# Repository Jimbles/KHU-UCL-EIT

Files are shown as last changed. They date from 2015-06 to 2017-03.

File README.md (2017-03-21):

# UCL KHU EIT MK2.5 MODS & MATLAB SOFTWARE

# CASE AND POWER SUPPLY

A new case and power supply had to be designed to enable the use of the 32 channel system inside a case without overheating. Included are the schematics and layout of the PCBs and the CAD drawings of the new cases

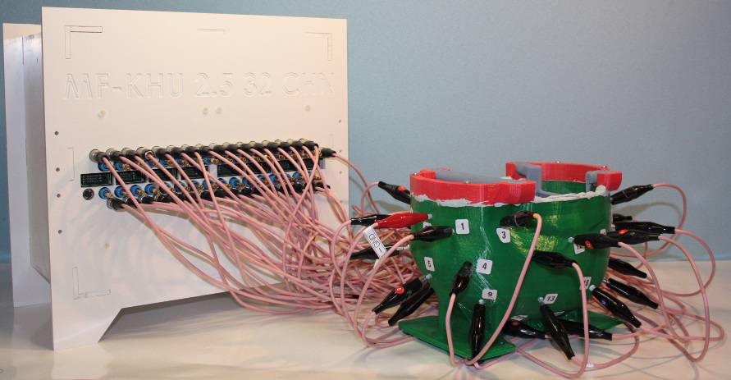
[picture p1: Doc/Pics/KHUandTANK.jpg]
khu and tank


# SOFTWARE

Software used in UCL group for making life a bit easier using the KHU Mk2.5 EIT system!

## Load_data

`khu_load.m` converts the data in a subdirectory into mV, as well as the protocol and other system settings. This is standalone, but can reference the .mat file made in `khu_makepairwise.m`

## Make_script

Most important script is `khu_makepairwise.m`, which creates the required script and proj file for the desired protocol/current/gain etc. 

## Calibration

These scripts load the calibration data located in the various .txt files generated by the KHU C++ GUI, and tries to apply some of the fuzzy logic/received wisdom from Bishal and other users

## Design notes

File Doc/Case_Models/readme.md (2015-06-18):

# 3D MODELS FOR CASE DESIGN

Included in this repo are .Step files created in Solidworks which were used to make the improved cases for the 16 chn and the 32 Chn KHU systems. All cases are made from plastic and all fixes are also insulating, so no metal parts are touchable

### 32 Chn Case

This case was cut out using a CNC machine from 4.5 mm ABS. The 4 inner pieces were glued together using acetone, with bracing pieces running along the inside edge. Drawings for CNC machine for both 32 system and power supply case found in Docs/Case_drawings ``32-CNC-Assembly.pdf``

### Power Supply Case

Constructued using similar methods to system case, with all but the lid stuck togther with bracing. To screw the lid on, corner pieces ``32PowerCaseCNR`` were 3D printed and an plastic nut added. These were then glued in all four corners with epoxy

### 16 Case
This was laser cut out of 4mm perspex - power supply could just about squeeze in the back. File used for laser cutting was ``16-Laser-assembly.pdf``

### Fans

In all cases the fans used were San Ace 120 model num ``9S1212M4001`` from farnell. These run at 12 V, so another XP Power AC/DC converter was added to the power supply case, with a separate connection to the system case

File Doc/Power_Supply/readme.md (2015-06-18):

# POWER SUPPLY

These are an adaptation of the existing power supply design, but with improved heat dissipation on the power transistors and higher current gain. A more detailed description is given in ``Power_Supply_Report.docx``

These were designed for the 32 Channel system, however they can just as well be used for the 16 Channel, and may even be beneficial

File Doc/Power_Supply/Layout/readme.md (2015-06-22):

These are the layouts of the boards designed in OrCAD. Also included are versions converted into Allegro PCB editor types, but these did not convert without problems...

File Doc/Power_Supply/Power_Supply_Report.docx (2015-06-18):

32 Channel KHU Mark 2.5 Power Supply

1. Power Supply Requirements for the 32 channel KHU Mark 2.5 system:

| Digital backplane | Analog backplane | DSP
Voltage (V) | 3.3 | +5, -5 | 5 or 7
Current (A) | 8 to 9 | 3 to 4 | 0.15 to 0.2

2. Problems with the old power supply:
- It was primarily designed for the 16 channel system hence it was unable to meet the specifications of the 32 channel system
- Since the system is power intensive, the heat dissipation is quite high. As no fans or any cooling mechanisms were included in the design, it resulted in components failure and poor performance.

Thus, the power supply had to be redesigned, building on the design of the older one.

3. Power supply design

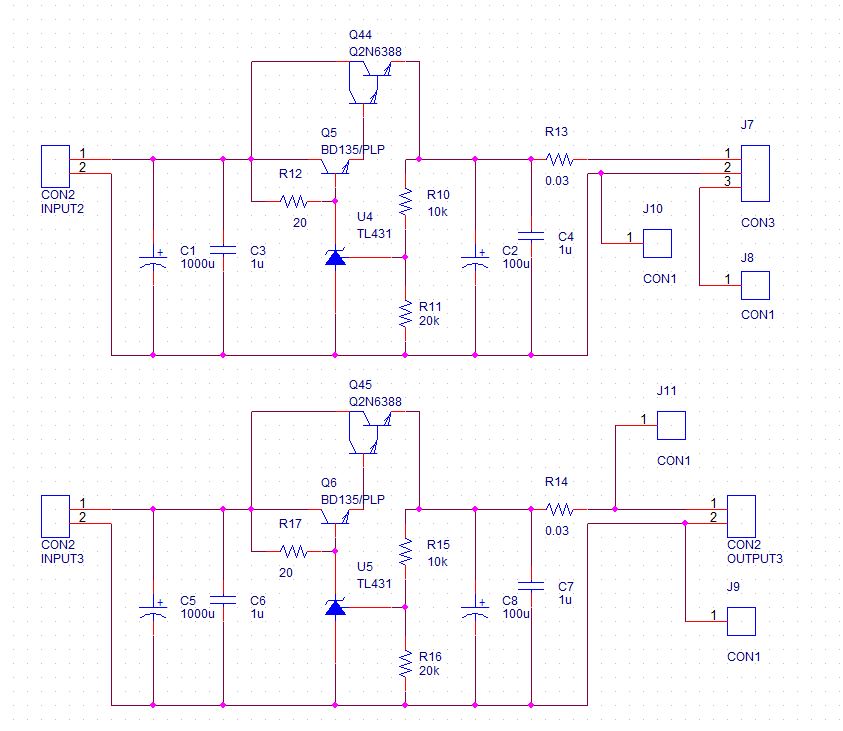
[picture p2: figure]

Figure 1: 3.3V digital power supply

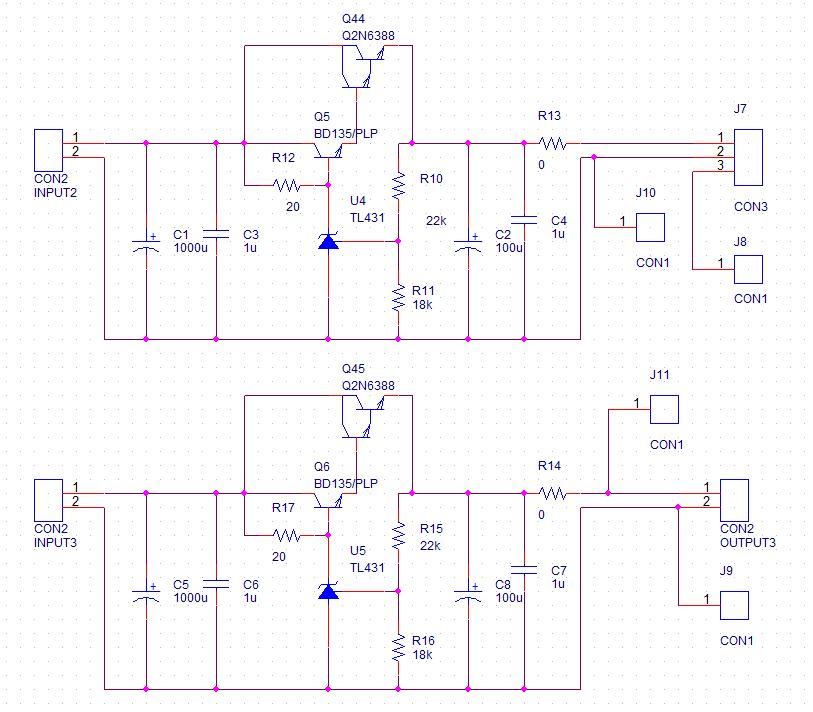
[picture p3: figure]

Figure 2: +/- 5V analog power supply

Same switching mode power supply (SMPS) modules used in the previous design were used in this new design as well. ECM100US07 (7V, 100W) is used to supply the digital backplane and the DSP, ECM100US09 (9V, 100W) is used for the analog backplane and ECM100US12 (12V, 100W) for the fans in the power supply case as well as the KHU system case.

Figure 1 and 2 show the circuits to regulate the outputs from the SMPS to meet the requirements for the system. The design is essentially similar to the older one with the exception of the capacitors and the transistors used. In order to meet the required amperage, transistors BD135 and 2N6388 were used in darlington pair configuration. 2N6388 is a single chip darlington transistor in itself.

Figure 1 and 2, which are for the digital and analog supply respectively, differ only in the value of resistors used. Two circuits in figure 1 are used in parallel to provide the higher amperage for the digital supply, hence the 0.03 ohm, 3W resistor is included at the output to balance the current. The circuits in figure 2 should be connected in series in order to obtain the +5V, GND and -5V required for the analog supply. As evident from the circuit, this is achieved by connecting J10 to J11 and J8 to J9.

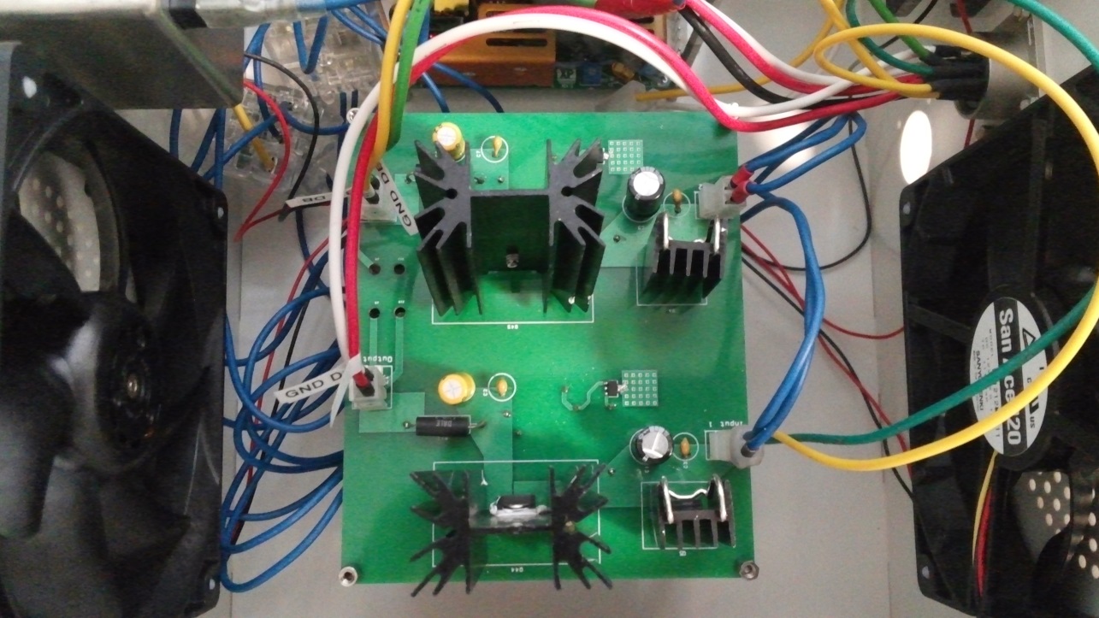
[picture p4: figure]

Figure 3: Circuit board for 3.3V supply

The layout for the circuit board has been designed to suitably accommodate the components which include large heatsinks for 2N6388, and to provide ample space for the high current path.

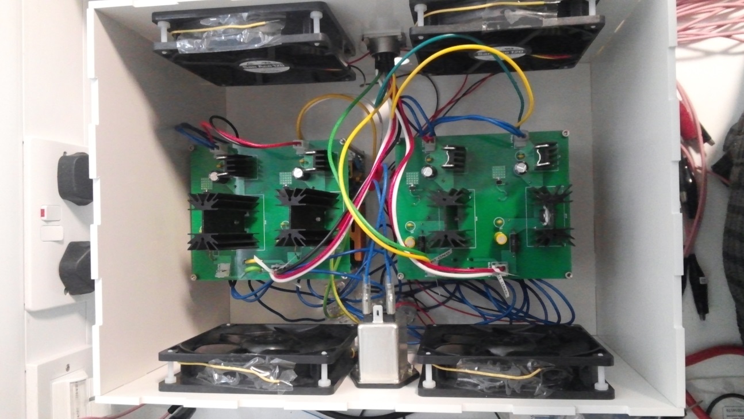
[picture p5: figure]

Figure 4: The power supply in its entirety

Two ECM100US07 modules are used to power the digital supply and two ECM100US09 modules are used to power the analog modules. One ECM100US07 is used to power the DSP. The outputs of ECM100US07 are adjusted to be 6.5 V and outputs of ECM100US09 are adjusted to be 8.5V using the potentiometer in the modules. This is done in order to reduce the power dissipation at the transistors.

Four fans are used for cooling the power supply as seen in figure 4. The fans are rated at 12 V, 0.13 A each. ECM100US12 is used to power the fans.

4. Comparisons with old power supply

Figure 5: Comparison between old and new PSU when KHU system is idle

Figure 6: Comparison between old and new PSU when KHU system is scanning

The performance of the new power supply shows significant improvement over the old one as shown by figure 5 and 6. This data was collected from the +5V and GND pin on one of the analog backplanes for the 32 channel system.

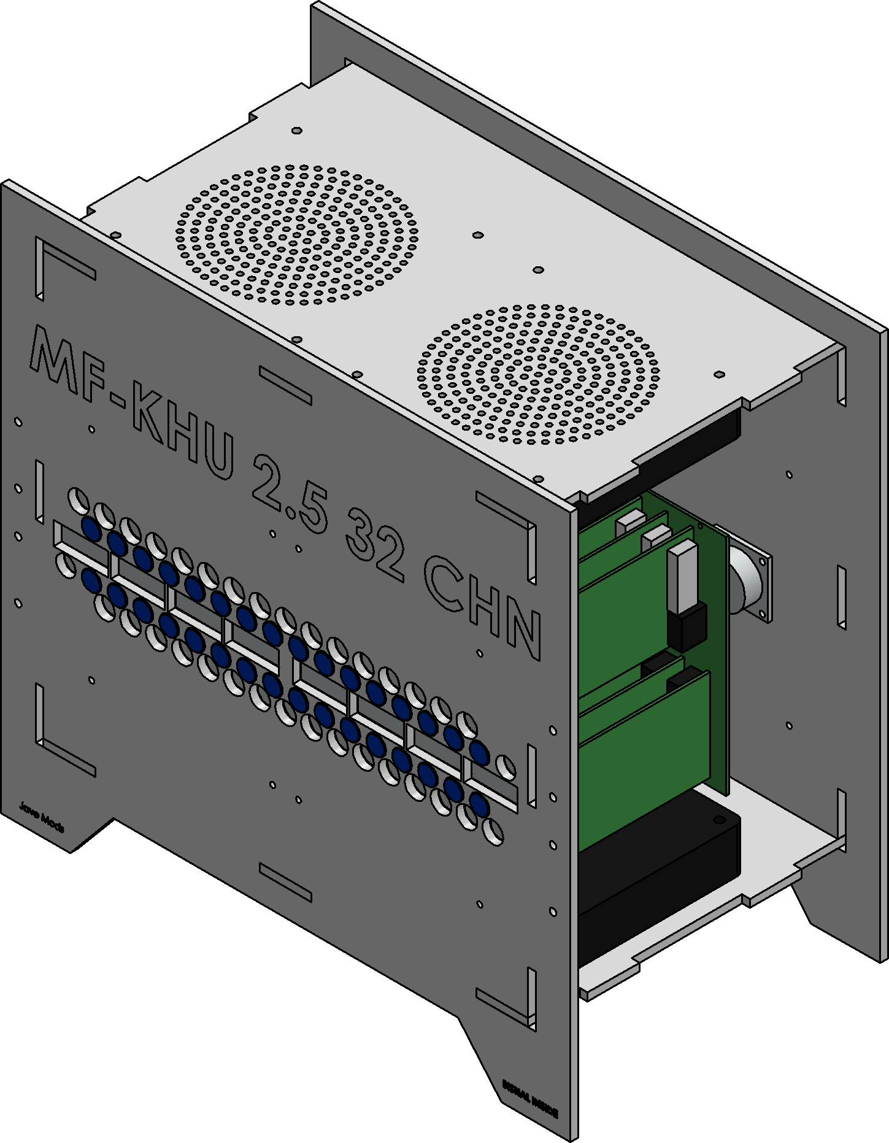
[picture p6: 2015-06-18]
Doc/Pics/32SystemCase.png

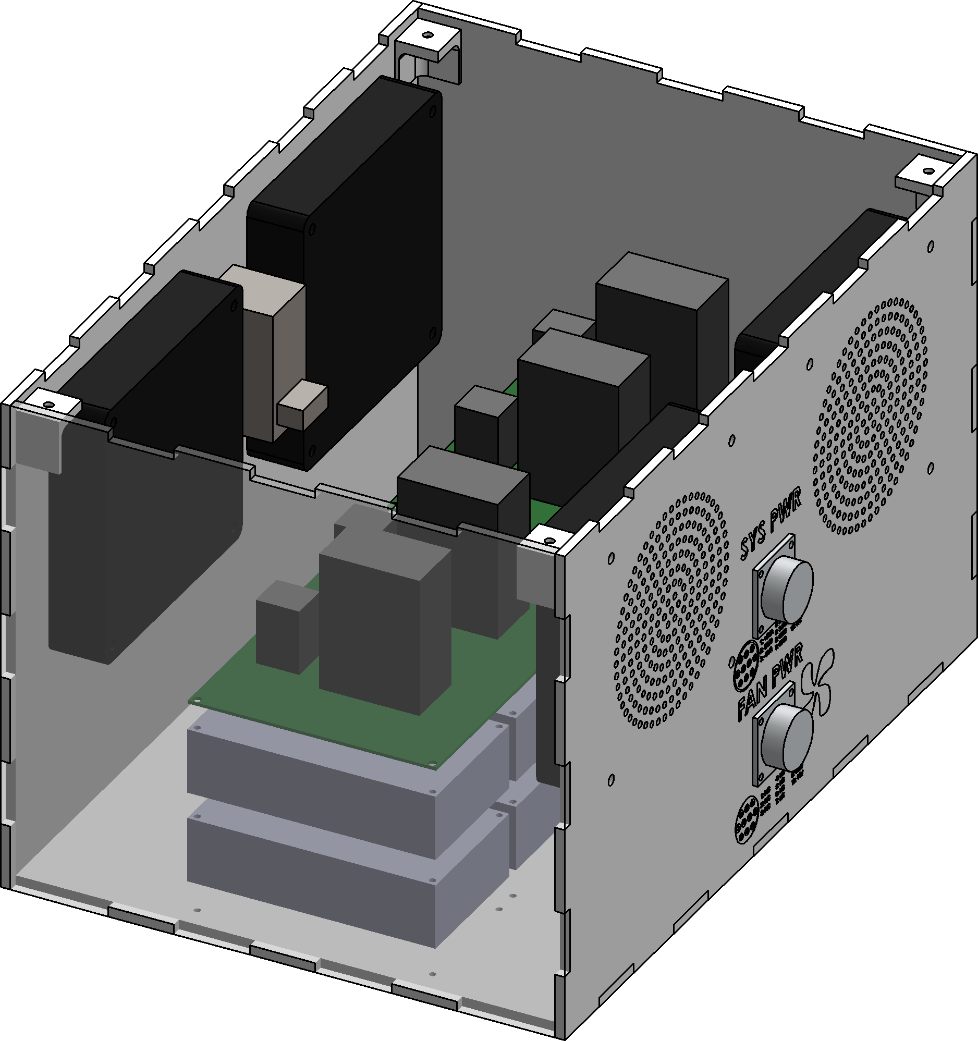
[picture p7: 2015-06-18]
Doc/Pics/32PowerCase.PNG

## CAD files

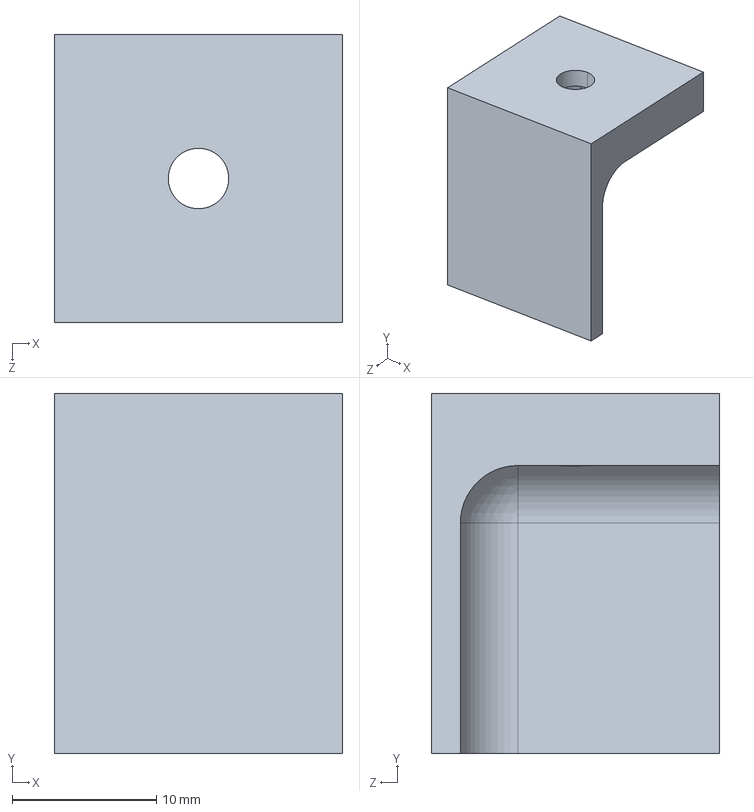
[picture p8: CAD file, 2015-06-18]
Doc/Case_Models/32PowerCaseCNR.STEP
20.0 x 25.0 x 20.0 mm

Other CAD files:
Doc/Case_Models/32PowerCaseCNR.STL

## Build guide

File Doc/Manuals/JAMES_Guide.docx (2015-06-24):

# KHU EIT MK 2.5 Calibration Procedure and System Check

This document is supposed to be used in conjunction with the manual given by Kyung Hee, which describes the cabling setup etc. This guide is more of a best practice guide, and what to look for to check that the calibration is OK and how to check the system is connected fine.

# System Check – or what to do when you get “Total Ch: 0” errors

### First Sanity Check:

Is it even connected properly? Select “Devices and printers” from the start menu and you should have USBXpress device listed under unspecified devices

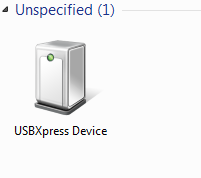
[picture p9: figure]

If that is OK then the next thing to do is check the IMM connection! If it is not, check the power to the DSP – is the light on at the back? (you will have to take the back of the case to see) Change the USB cable, check the power cable, restart the PC, try on another computer etc. etc.

## Check IMMs are recognised by the system

1. From the KHU software, select window > Engineer Control Dialog
2. On this dialogue hit USB Check, and the box to the left should change from 0 to 1.
3. Next hit Port Open, and the box should read Port Open

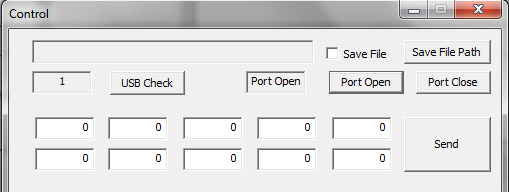
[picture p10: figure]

4. Next, with all 10 boxes with 0s in, hit send. This checks the communication is OK. The response should be: 129 and a load of zeros.

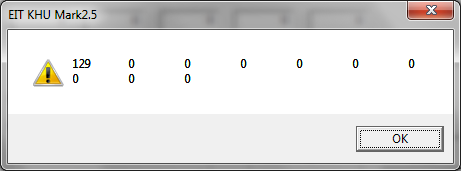
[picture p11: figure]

5. If that checks out, change the top left box to 2 and hit send like so:
6. And you should get the following response

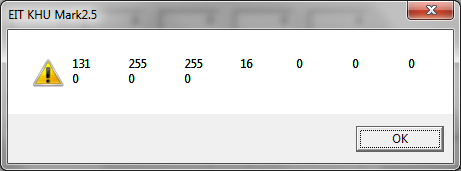
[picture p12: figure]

A little explanation:

131 is the response of the controller 129+2 (the command sent)

The next first two columns represent what channels of the digital backplane have IMMs in them as a binary number (1 for detected, 0 for undetected). The backplanes are split into 2 groups of 8, with the second column representing 1-8, and the third number representing 9-16. The response from each of the two groups is 25510 = 111111112, meaning an IMM was detected in each channel of the both groups. This is good. For example 19110 =101111112 means that an IMM was not detected in the 7th channel of that group. This is bad.

The next number are the total number of connected channels (i.e. ones with IMMs in them), which should be 16.

The final number is the total number of unconnected channels, and should be 0.

Summary:

131 | 255 | 255 | 16 | 0
System response | Group 1 connected IMMs | Group 2 connected IMMs | Total IMMs connected | Total unconnected channels

## What to do if you don’t get this!

The connections between the IMMs and the digital backplane are likely slightly loose. Take apart the system and rebuild it.

# Calibration

You have to do each of these steps for each frequency. The steps for this are pretty well documented in the proper manual.

## Order

The order in which you should perform the calibration is:

1. Output Impedance
2. DC Offset
3. Output Impedance
4. Amplitude
5. Voltmeters – Close the software afterwards. Known bug!

## Notes on cables

- Use the cables you are going to record with, i.e. the ones that will eventually be connected to the electrodes.
- Use the gold adaptors in the holes for the resistor phantom and the blue calibration channels to give something to crocodile clip on to.
- Use a short cable to connect the centre of the resistor phantom to the channel 1 or ground for amplitude and voltmeter calibration. Make sure this cable has good connection and low impedance
- The old KHU cables from the KHU MK1 and other systems, often had a resistor in the connector. So if you are using and old cable, unsolder this from the connector first

## What to check – did it calibrate OK?

The results of all of the calibrations are stored in the folder “1234” in the folder “Calibration” found in the same folder where the KHU software is stored. Within the Calibration folder look for separate folders for Amplitude, DCOffset, OutputImpedance and Voltmeter tests, as well as subfolders for each frequency.

### Output Impedance

Choose the folder corresponding to the frequency you are calibrating at, and look at the files in Log > Zout. You should see something like this:

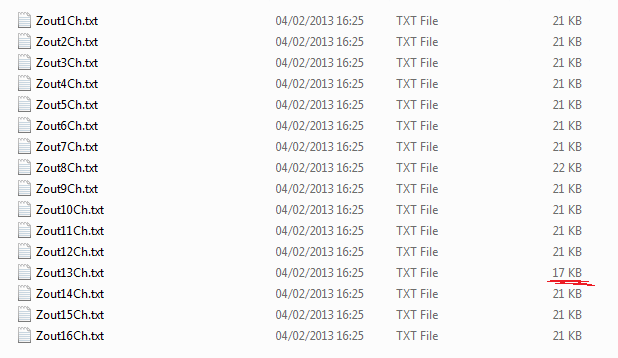
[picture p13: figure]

With a separate text file for each IMM. The first sanity check is the file size, every test is doing exactly the same thing with the same number of results, so the files should roughly be the same size. Channel 13 had a problem with the connection during this test, and this is shown by the smaller file size of 17KB as instead of 16bit numbers the results were “INF”.

Open up of these files and scroll down to the very bottom line and if all is well you should see: MaxZout: 1e+009.

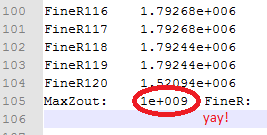
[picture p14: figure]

i.e. that the maximum output impedance was measured to be 1 MΩ. Check this for all channels before moving on.

#### If you don’t get this

Check the connections are ok, it’s usually something simple like the cables aren’t connected ok or the cable is broken. Occasionally, you might not reach an output impedance that is exactly 1MΩ but after performing the DC offset calibration and repeating this output impedance calibration can give you the correct result. If not – swap the IMMs around and see if it is consistent with the channel or the IMM.

### DC Offset

Check the DCOffset.txt in the folder corresponding to the frequencies you are interested in. What you are looking for are similar values, and only small changes – the fuzzy logic is less than 25ish with certainly no 3 digit changes.

### Amplitude

Look for the file Amplitude.txt in the folder corresponding to your frequency of interest. The first value should be 1, and the remaining values should be closed to 1, as this indicates only small adjustments to the current levels were needed. This is very sensitive to the connection to the centre of the resistor phantom, so make sure this cable is OK

### Voltmeter Calibration

The best way to check this is correct is to collect a few test frames on the resistor phantom, and compare the results with the simulation/expected results. CLOSE THE SOFTWARE AFTER VOLTMETER CALIBRATION. There is a known bug which means you can’t start scans after running that dialogue.

YOU MUST USE THE CORRECT SIMULATED VOLTAGES.

The voltmeter gives the correction factors to convert from the demodulated digital values to the simulated values (in either mV or V, or anything you choose) and to give a phase angle of 0. This includes the gain correction. Thus, if you change the gain in the protocol, you must recalibrate the voltmeters. If you change the current injection, you must first change the simulation to represent the new current level, then create a new file with the expected values, then recalibrate the voltmeters.

#### Making new simulated voltages

The model of the resistor phantom can be found in circuitlab:

https://www.circuitlab.com/circuit/m5cv9k/khu-resistor-phantom/

or as a OrCAD file in the technical folder of eit-nas.

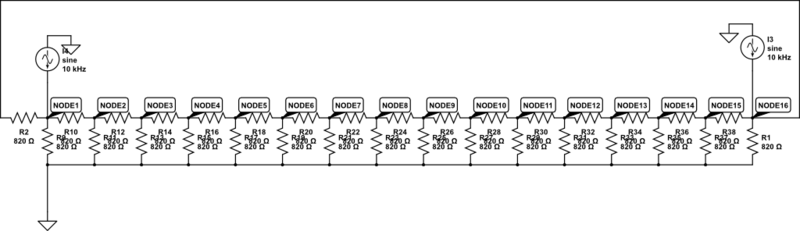
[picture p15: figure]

In this model each node represents the differential voltage between the two channels, i.e. what is measured by the system. These do not change with different protocols. So what you are interested in changing is the two current sources. These in the above picture, ch1 is the source and ch16 is the sink. The source is set to 1000uA and the sink is set to -1000uA. Change the amplitudes and the positions which match the protocol you are using, and then simulate the resulting voltages.

To get the simulated voltages into matlab to check:

1. On circuit lab, switch to the simulate panel and choose “time domain”
2. Hit “Run Time-Domain Simulation” an d you should get something pretty like this:

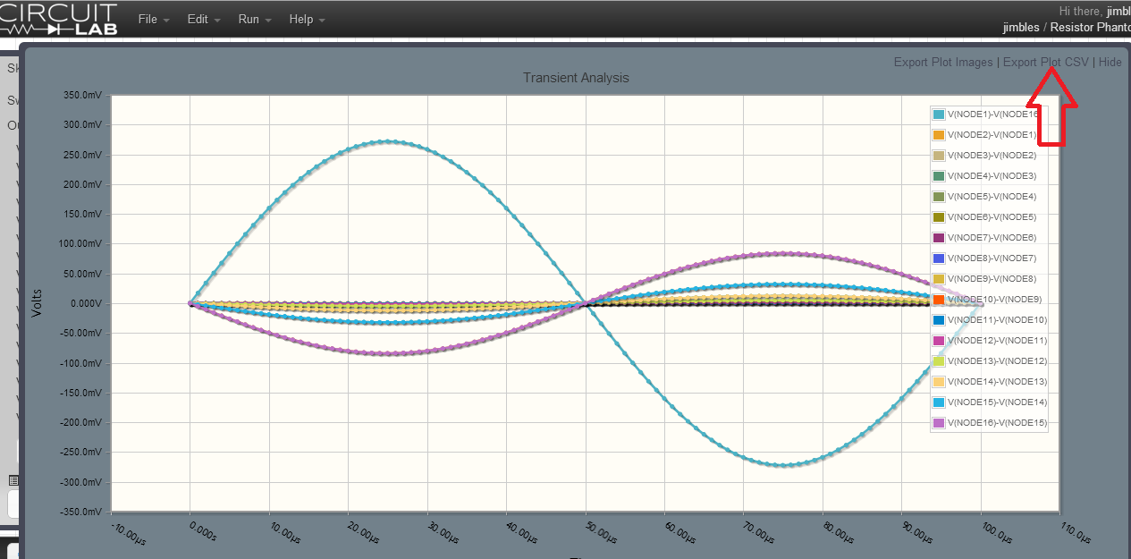
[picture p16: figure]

3. Hit Export Plot CSV and copy the text in the box that pops up to the clipboard
4. In matlab, type uiimport and then select “clipboard”, make sure comma is selected as the delimiter
5. The format of this data is then:

Time | Chn1 | Chn2 | Chn etc.

6. So to find the correct voltages for calibration find the max in each channel: max(data(:,2:end))
7. Do this for every current injection you have in your protocol
8. Make a text file in the same format as the others e.g. 2Dneighboring_mV.txt where each column is an injection pair, with a row for each channel.

# Building the system

1. Attach all the IMMs to the digital backplane
2. Holding the backplane in one hand with the IMMs vertically, align the bottom connection of analogue front plane with lowest row of 8 IMMS with the other
3. Push the IMMs together ensuring all the connectors are aligned and snapped together. This can be tricky!
4. Push the whole system together above each IMM connection with the palms of your hands
5. Attach the DSP module, check that the USB connector is parallel to the plane of the IMMs and that the pin numbers connectors on the backplane and the DSP board are matching.
6. Test the power levels are correct before connecting the system
7. Connect the power cable and test that all IMMs are recognised.
8. Unplug the power and put system in case
9. The PCB standoffs required are as followed
10. Correct PCB standoff sizes:

Front of case

10mm

Analogue backplane – 2mm

45mm

30mm

30mm

7mm

Digital backplane – 2mm

25mm (this one is optional)

7mm

Back of case

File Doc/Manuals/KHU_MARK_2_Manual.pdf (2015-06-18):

# KHU MARK 2.5 - USER MANUAL

## Contents

## I. System Description | 2

## II. Electrical Characteristics | 4

## III. Installation | 5

## IV. Operation Manual | 6

## 1. Normal mode – Single Frequency | 6

## 2. Normal mode – Multi Frequency | 8

## 3. Normal mode – Single Frequency | 6

## 4. Users configurable parameters | 10

## V. Data format | 13

## VI. Calibration | 14

## 1. DC offset calibration | 16

## 2. Output Impedance calibration | 17

## 3. Amplitude calibration | 18

## 4. Voltmeter calibration | 19

I. System descriptions

Similar to KHU Mark2 system for Electrical Impedance Tomography measurement, the KHU Mark 2.5 has two separate units, one for power supply and one for EIT data acquisition.
Current KHU Mark 2.5 is a 16- channels system with integrated calibration. Impedance measurements controller and calibration are PC-controlled through a software called EIT_Mark2.exe. It is currently only available for Windows (64 and 32 bits).

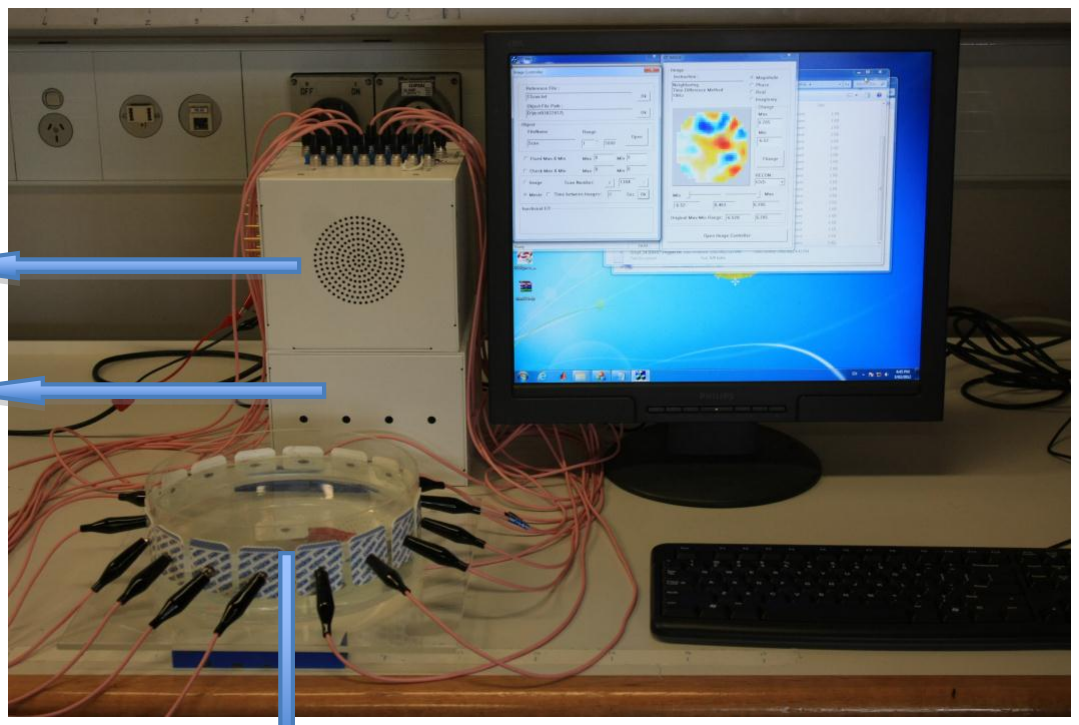
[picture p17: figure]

Figure 1 KHU MARK 2.5 system

Main KHU Mark2.5 unit consists of 16 parallel IMMs (Impedance Measurement Modules), an analogue backplane, a digital backplane and a DSP mainboard. Analogue backplane is used to switch the IMMs between current injection and voltage measurement. Digital backplane communicates between the IMMs and DSP. Each IMM consists of a CCS( constant current source) , CCS Calibration circuits, ADC (12 bits resolution), Voltage amplifier circuits and an FPGA as the central control unit for each IMM.

Main part

Power Module

Saline tank

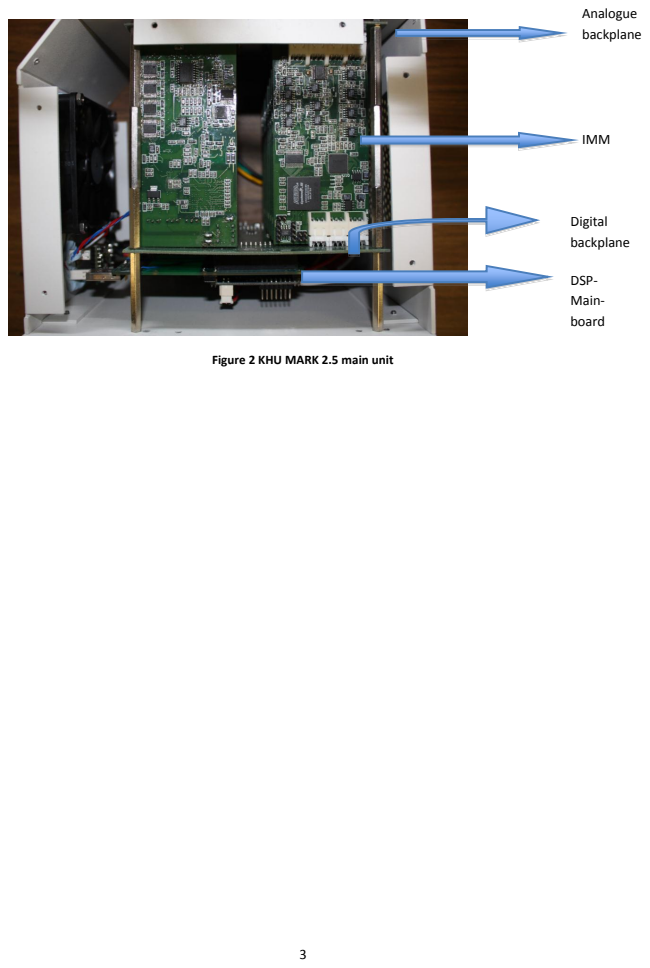
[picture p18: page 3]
IMM; Digital backplane; DSP- Main- board; Analogue backplane

Figure 2 KHU MARK 2.5 main unit

II. Electrical characteristics

### 1. Power

| The KHU Mark 2.5 is medically (?) electrically isolated to avoid electrical shock in clinical settings. The power unit provides three different types of powers to the main unit:
- ±5 VDC at 2A (max) for the analogue backplane
- + 3.3VDC at 6A (max) for the digital backplane
- +5 VDC at 1A (max) for the DSP main-board
| If the power is not functional, the following sequence should be used to provide power for the main unit of the KHU Mark 2.5 system:
- Step 0, connect main unit to PC through USB port
- Step 1, turn the ±5 VDC (2A max) on for the analogue backplane
- Step 2, turn the +3.3 VDC (6A max) on for the digital backplane
- Step 3, turn the +5 VDC (1A) max on for the DSP main-board
| When turning off the system while on lab power supply, turn off each unit in the reverse order of turning on.

### 2. Signals

- 16 parallel channels.
- 1 GND electrode
- Max current injection from each channel is 1mA
- Contact impedance (to be completed)
- Trigger signal: TTL at +3.3 V, high impedance matching (~100 kΩ)
- Operating frequencies: 10 Hz, 50 Hz, 100 Hz, 1kHz, 5kHz, 10Khz, 50KHz, 100KHz,
| 250 kHz and 500 kHz.
- The actual digital output frequencies are 11.25 Hz, 56.25 Hz, 112.5 Hz, 1.125 kHz,
| 5.625 kHz, 11.25 kHz, 56.25 kHz, 112.5 kHz, 247.5 kHz and 450 kHz.

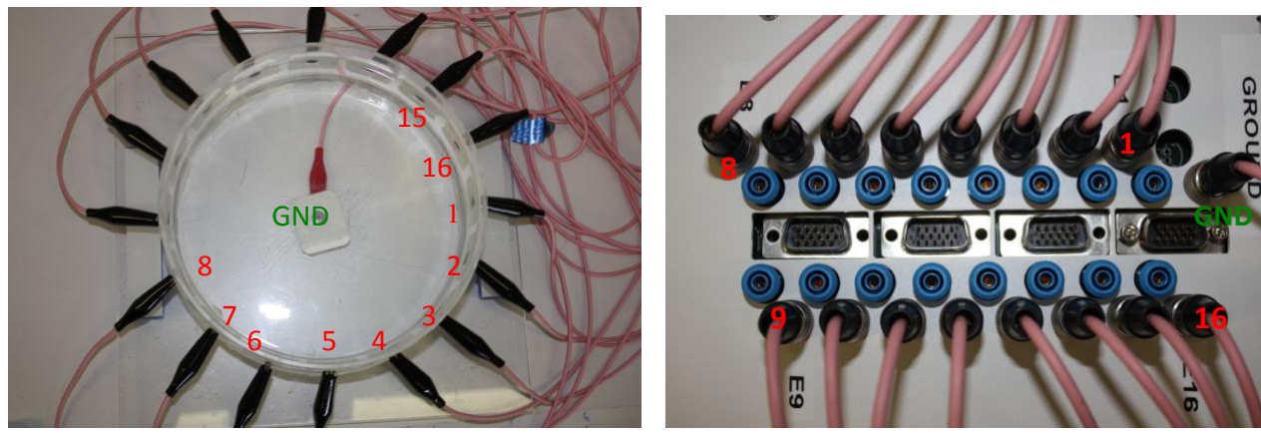
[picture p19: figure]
GND
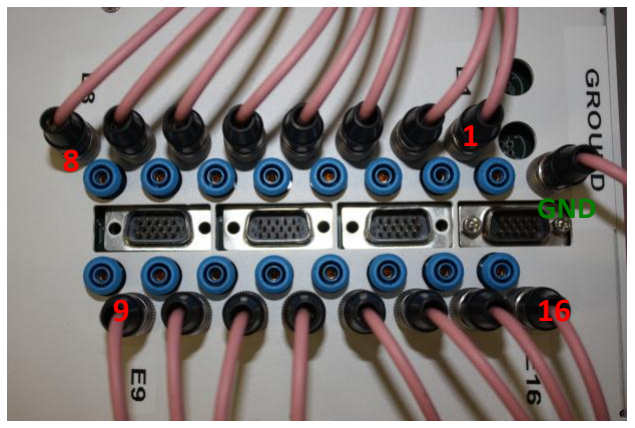
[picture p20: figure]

Figure 3 Electrodes placements on simulation tank and KHU Mark 2.5

III. Installation

### 1. USB Driver installation

USB driver of the KHU Mark 2.5 should be installed through the following steps:

1. Uninstall any preinstalled USBXPress driver
2. Run the executable USBXPress.exe. This should create and copy files to a folder at C:\SiLabs\MCU\USBXPress

In case there is no "SIUSBXp.dll" in C:\WINDOWS\system, copy SIUSBXp.dll from C:\SiLabs\MCU\USBXpress\USBXpress_API\Host to C:\WINDOWS\system

3. Run C:/SiLabs/MCU/USBXpress/Driver/Preinstaller.exe
4. Connect the system (MARK 2.5) to USB port
5. | When | the | windows | popup | asking | for | new | driver, | add | the | path
C:/SiLabs/MCU/USBXpress/Driver to find driver
6. Done. Windows should report driver for device installed properly.

Note that only the most current USBXPress driver (version < 3.5) would work in a Windows 7, 64 bits.

### 2. Setup KHU Mark2.5

i. Connect the power unit to the main unit (power should be off)

ii. Connect the main unit to PC via USB port

iii. Connect power unit to power plug (make sure power button is still off)

iv. Turn power on

v. Open the controlling software EIT_Mark2.exe

IV. Operation manual

### 3. Normal mode – Single frequency

i. EIT_Mark2 main window should look like this.

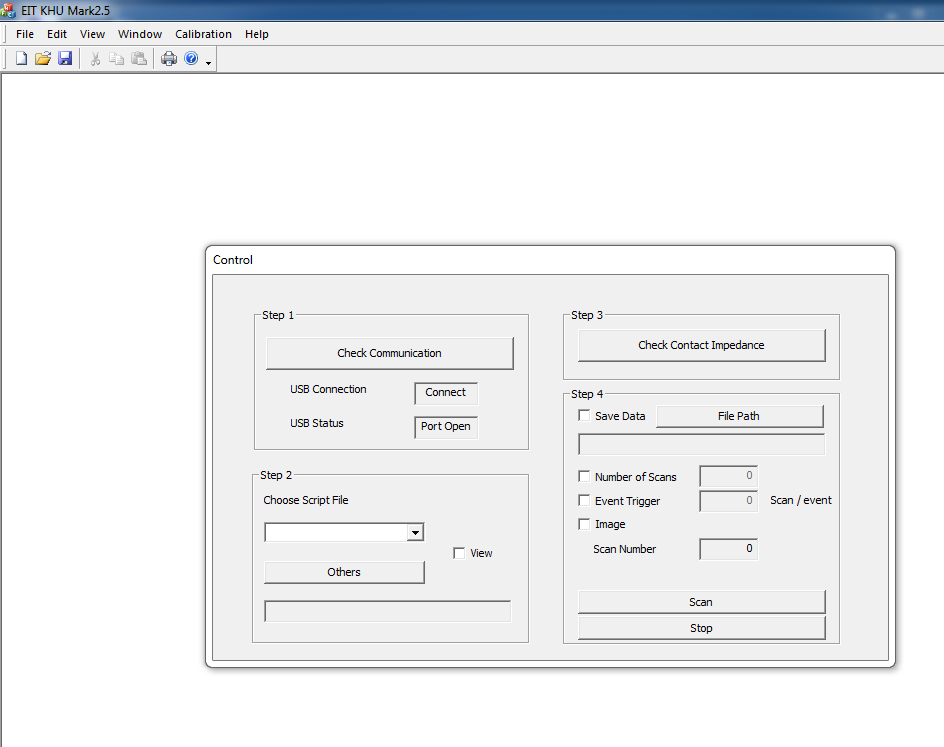
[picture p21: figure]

ii. Follow the steps on the main control dialog to setup the projections prior to scanning:
a. Step 1. Check communication, make sure the USB connection is Connected and USB port status is Open
b. Step 2. Load the correct script file with desired frequency, projection protocol, amplitude and all the calibrations are ON. An example script file is included below.

%Date 10/22/2010

%Comment :

#include "projection\projection_7.50kHz.txt"

start

setting

Channel | 16 // Number of channel
Average | 64 // Number of average
Freq | 1 | // Number of frequency
TimeInfoHigh | 0 | // Delay between projections (High byte)
TimeInfoMid | 7 | // Delay between projections (Mid byte)
TimeInfoLow | 0 | // Delay between projections (Low byte)
InjDelayHigh | 0 | // Delay from the press of Start button to
| | the start first scan (High byte)
InjDelayLow | 60 // Low byte of the above quantity

stop

calibration

DCOffset | ON
OutputImpedance | ON

Amplitude | ON
Voltmeter | ON
Protocol | 2DNeighboring_mV

stop

scan

projection1

projection2

projection3

projection4

projection5

projection6

projection7

projection8

projection9

projection10

projection11

projection12

projection13

projection14

projection15

projection16

stop

end
c. Step 3 Check contact impedance – Make sure that the voltage is not overflowed.
d. Step 4
- Check the appropriate boxes to Save data (in appropriate File Path)
- Check the box for Number of Scan and specified and the desired number of scans
- In normal mode, the Event Trigger box should be left unchecked.
- Check the Image box to view real time images. If this option is checked, during data acquisition, images are concurrently reconstructed. Typically, the first 5 scans contains transient noise and therefore are discarded (not saved). The reconstruction algorithm uses the first saved frame of data as its homogeneous or baseline data. Subsequent scans are reconstructed against the homogeneous data. Notably, the reconstruction software assumes that the object is circular, with the first electrode at 3 o’clock and electrodes are arranged clockwise.
e. Step 5 - Click Scan to start scanning, if the Image box is checked, it should look like this

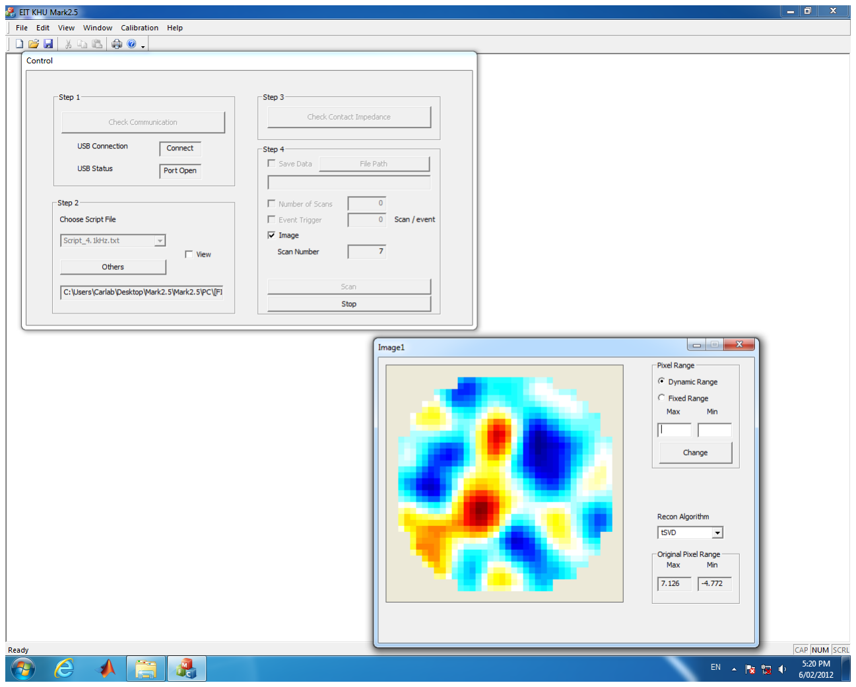
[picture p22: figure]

### 4. Normal Mode – Multi-frequency

a. Multi-Frequency mode

One main difference of KHU MARK 2.5 from KHU Mark1 is that each IMM has independent current source so that each channel can independently generate current waveform. One option is the Multi-frequency mode. As you are able to check in a projection file, injecting one frequency at one pair of channels and another frequency at the other pair of channels at the same time. Due to the fundamental method of wave generation, we have harmonic problem at Multi- frequency mode. In order to minimize this effect, it is recommended to use one pair and the other pair at the opposite end such as 1 and 16 for one frequency, 8 and 9 for the other.

Due to the limitation of bits of demodulation frequency (6-bit), it is not possible to produce concurrently produce two frequencies that have a ratio (f1/f2) of more than 50.

Multi-frequency mode can be selected in the projection.txt file. An example is shown in the following figure.

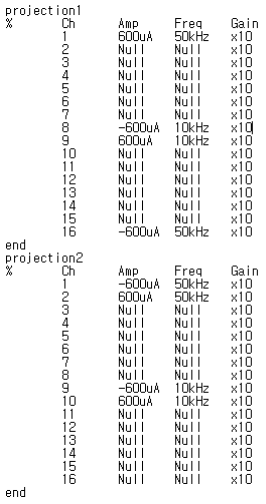
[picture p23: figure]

b. Mixed-Frequency mode

The other option of independent current source is Mixed Frequency mode. It is possible to generate the waveform by mixing three frequencies together in one channel. The ratio of frequencies in each mix is fixed at 1:5:10. Accordingly, there are four combinations from the range of operating frequency such as 10Hz, 50Hz, 100Hz (called as MIXED1), 1kHz, 5kHz, 10kHz (called as MIXED2), 10kHz, 50kHz, 100kHz (called as MIXED3), 50kHz, 250kHz, 500kHz(called as MIXED4).

In terms of GIC, the current output is connected to the GIC for smallest frequency, for example GIC3 for MIXED4.

To select mixed-frequency mode, a mixed combination (e.g MIXED1) should be entered in place of frequency in a projection.txt file, as shown in the following figure.

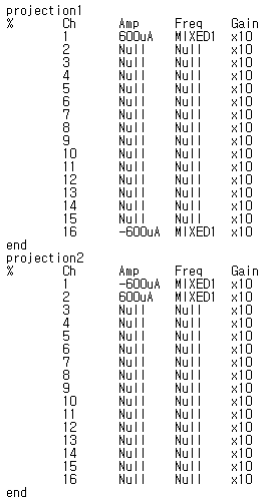
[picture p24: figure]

### 5. Biopotential triggering mode

a. Triggering signal requirements
- TTL interface (3.3 VDC)
- 5ms pulse width
- 1 Hz
b. Parameters
Inj Frequency | No Average | TimeInfo | TimeSlot | Max Frame/s
10 kHz | 1 | 0-0-127 | 1 (corr. 20 ms) | 50
50 kHz | 1 | 0-0-127 | 1 (corr. 20 ms) | 50
c. Procedures
i. Follow all the steps for normal operation mode
ii. Check the Event Trigger box
iii. Specify the number of Scans/trigger. If number of Scans/trigger is not specified, the default value is 1.
iv. Press Start to start scanning.

### 6. Users configurable parameters (in script.txt and projection.txt)

a. Script file

Users can change following quantities in the script.txt file:
-Average: Number of averages taken per voltage measurement. Minimum average is 1 and maximum is 64 and averages must be power of 2.

-Frequency: Number of frequencies to be used in each projection. This quantity should be 1 for single frequency measurement, 2 for multi-frequency mode and 3 for mixed-frequency mode.

-TimeInfoHigh and TimeInfoLow: Delay between projections. This is a 16 bits value. The first (HIGH) byte is specified in TimeInfoHigh while the second (LOW) byte is specified in TimeInfoLow.

-InjDelayHigh and InjDelayLow: Delay from the press of Start button (in the control dialog) to the start of the first scan. Similar to TimeInfo, it is a 16-bit value, specified by InjDelayHigh for the HIGH byte and InjDelayLow for the LOW byte.

The following diagram shows the timing of the system:

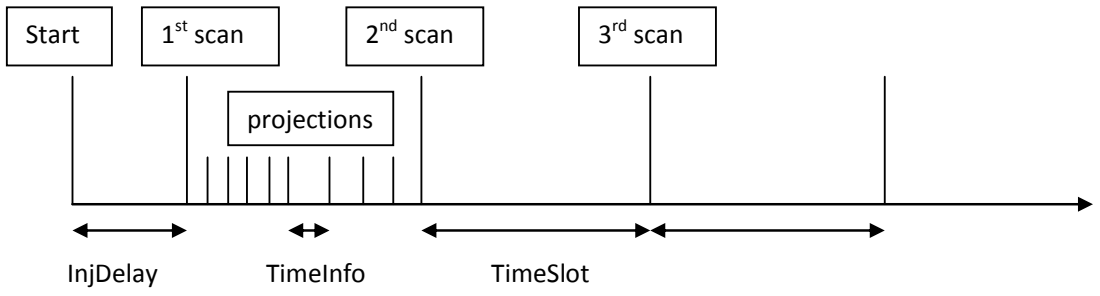
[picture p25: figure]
Start; st scan; nd scan; projections; InjDelay; rd scan; TimeInfo; TimeSlot

The InjDelay in real time min value is 80us and maximum is 360 us. Note that the values specified in the script.txt file for InjDelay and TimeInfo are digital values, not real time values.

The order of the projections can also be changed in script file.

b. Projection file
Each projection file contains the injection and measurement information for each projection, which should like this:

projection1
% | Ch Amp | Freq | Gain
1 | 600uA 50kHz x10
2 | Null | Null | x10
3 | Null | Null | x10
4 | Null | Null | x10
5 | Null | Null | x10
6 | Null | Null | x10
7 | Null | Null | x10
8 | Null | Null | x10

9 | Null | Null | x10
10 Null | Null | x10
11 Null | Null | x10
12 Null | Null | x10
13 Null | Null | x10
14 Null | Null | x10
15 Null | Null | x10
16 -600uA 50kHz x10
end
projection2
% | Ch Amp | Freq | Gain
1 | -600uA 50kHz x10
2 | 600uA 50kHz x10
3 | Null | Null | x10
4 | Null | Null | x10
5 | Null | Null | x10
6 | Null | Null | x10
7 | Null | Null | x10
8 | Null | Null | x10
9 | Null | Null | x10
10 Null | Null | x10
11 Null | Null | x10
12 Null | Null | x10
13 Null | Null | x10
14 Null | Null | x10
15 Null | Null | x10
16 Null | Null | x10
End

Typically, there are 16 projections for each frame, which are described in the projection file.

The users can change the injection pair, current injection frequency and the gain of each projection. The sequence of injection can also be changed as consequence.

Current injection amplitude and frequency can be changed in the projection file. Injection current amplitude ranges from 0 to1023 (digital value to be input): 0 digital value corresponds to 30 uA actual current amplitude, 1023 digital value corresponds to 1000 uA.

The gain is a digital value, specified the voltage gain of each voltage measurement. Minimum gain is 0 (which doesn’t mean a gain of 0). Maximum value for gain is 255.

Gactual =

40*Gdigital
200

V. Data format
Data obtained in each scan is recorded in an XXScan.txt file, saved in the folder specified in the File Path field (see Normal Operation – Single Frequency section). A part of a typical XXScan.txt would look like this:
0 | 1 | -26937.000000 | 30554.000000
1 | 1 | 26563.000000 | -30857.000000
2 | 1 | 3798.000000 | -1742.000000
3 | 0 | -1352.000000 | 1217.000000
4 | 0 | -1540.000000 | -235.000000
5 | 1 | 1545.000000 | 1705.000000
6 | 0 | -2219.000000 | 183.000000
7 | 0 | 2701.000000 | -2473.000000
8 | 0 | -933.000000 | -218.000000
9 | 0 | 566.000000 | -595.000000
10 | 0 | 151.000000 | 983.000000
11 | 0 | 841.000000 | -1982.000000
12 | 0 | -1714.000000 | 1780.000000
13 | 0 | -298.000000 | 48.000000
14 | 1 | -0.000000 | -0.000000
15 | 1 | 27005.000000 | -30445.000000

Each text file contains the data of each full frame, typically consists of 16 projections for single frequency measurement mode. The above is data obtained from one projection.
- The first column is the number of measurement: 0 is the measurement between electrodes 16 and 1, 1 is measurement between electrodes 1 and 2 and so on.
- The second column contains binary values indicating whether the corresponding voltage measurement is saturated (1) or not (0). Voltage measurements are usually saturated at the measurements involving the current injection electrodes.
- The third column contains the real values of the corresponding measurements
- The fourth column contains the imaginary values of the corresponding measurements.
In the current version of the EIT software, if multi-frequency mode is selected (specified in projection.txt file), the data is stored for the lowest frequency first (16 measurements x 16 projections), a blank line, then the data for the second lowest frequency (16 measurements x 16 projections) and so on. In total, there are 16 measurements x 16 projections x N number of frequencies.

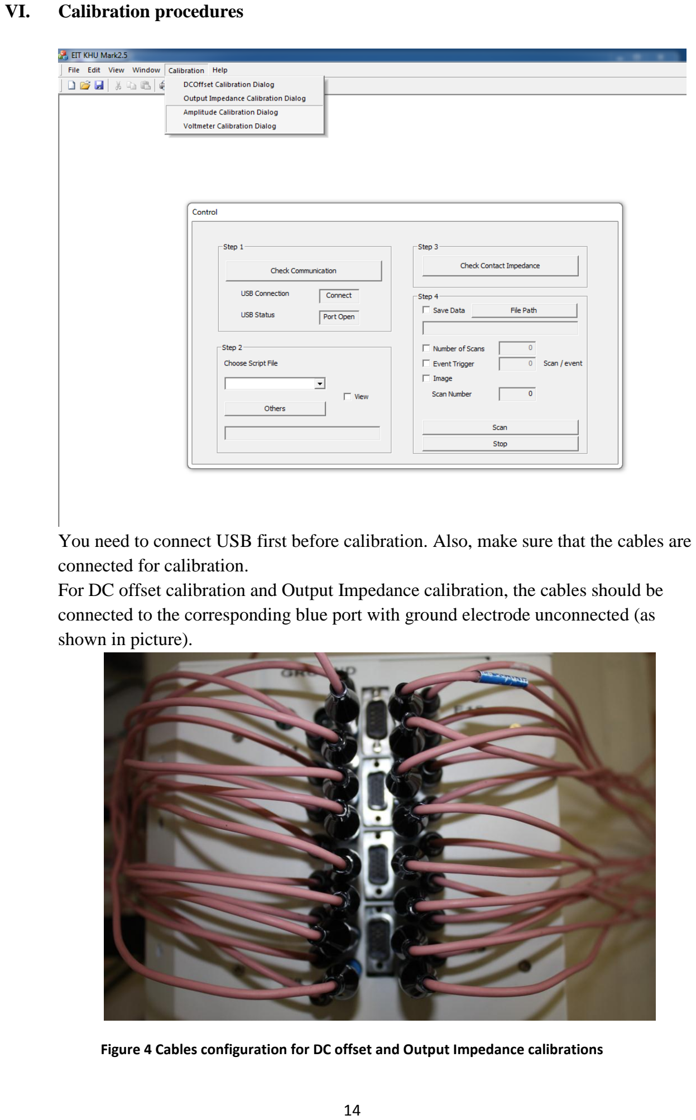
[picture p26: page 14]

VI. Calibration procedures

You need to connect USB first before calibration. Also, make sure that the cables are connected for calibration.
For DC offset calibration and Output Impedance calibration, the cables should be connected to the corresponding blue port with ground electrode unconnected (as shown in picture).

Figure 4 Cables configuration for DC offset and Output Impedance calibrations

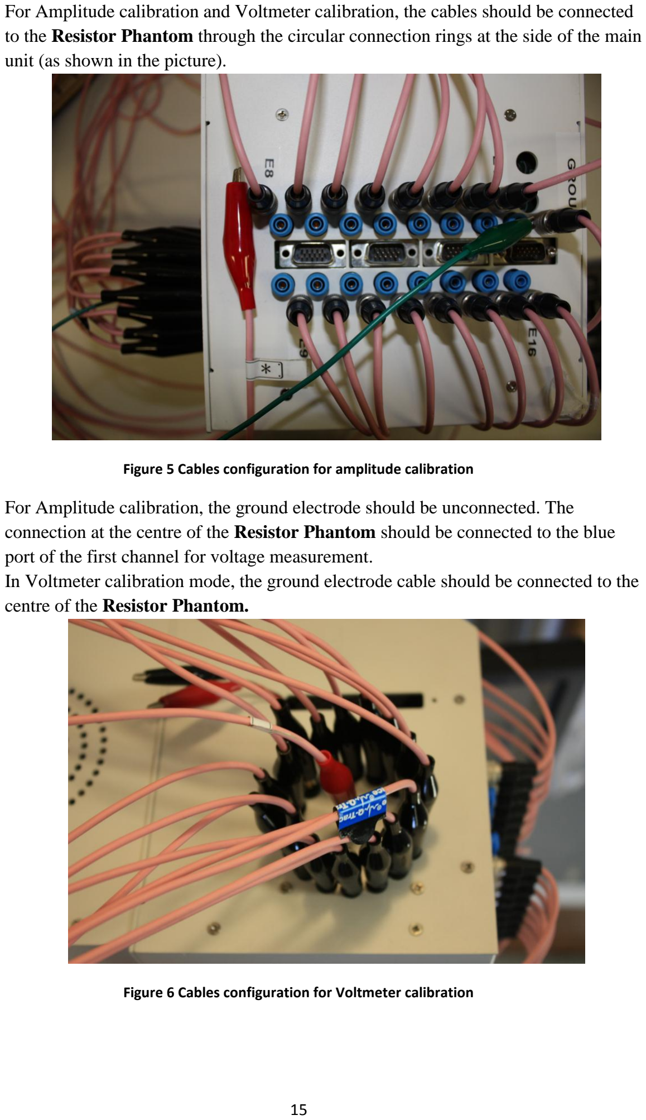
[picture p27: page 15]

For Amplitude calibration and Voltmeter calibration, the cables should be connected to the Resistor Phantom through the circular connection rings at the side of the main unit (as shown in the picture).

Figure 5 Cables configuration for amplitude calibration

For Amplitude calibration, the ground electrode should be unconnected. The connection at the centre of the Resistor Phantom should be connected to the blue port of the first channel for voltage measurement.
In Voltmeter calibration mode, the ground electrode cable should be connected to the centre of the Resistor Phantom.

Figure 6 Cables configuration for Voltmeter calibration

### 1. DC offset calibration

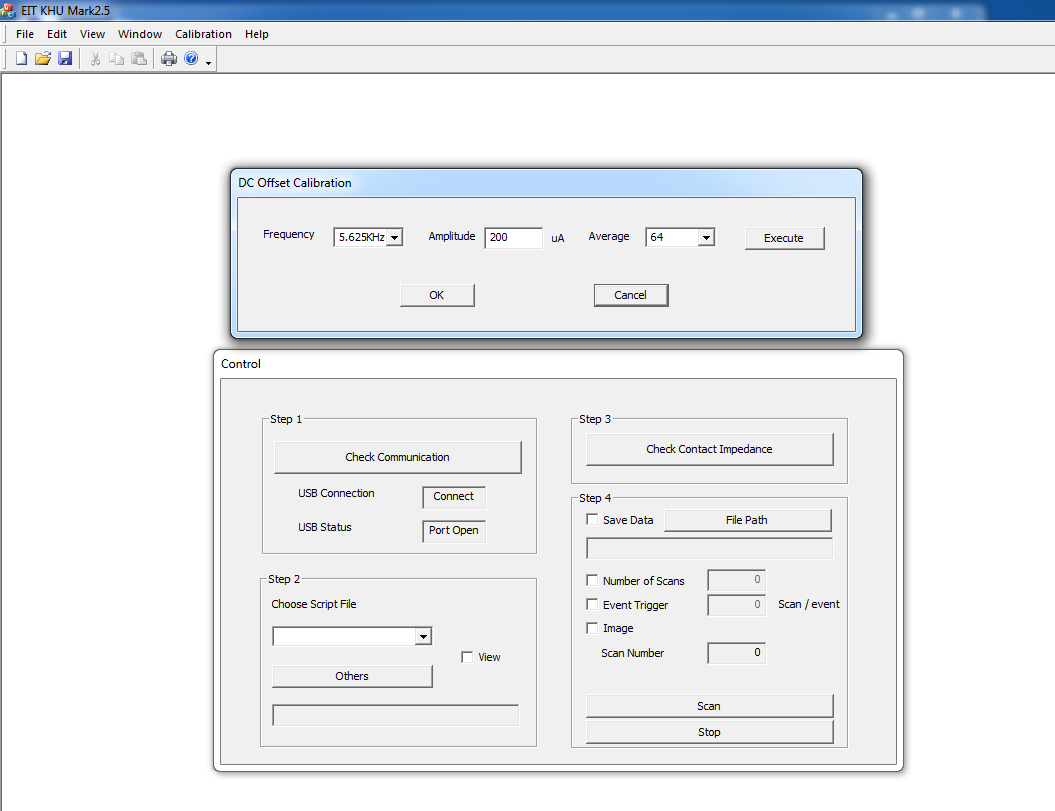
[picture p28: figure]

ii. Select frequency you want to calibrate.
iii. Set current amplitude of waveform. Default value is 200uA. It is recommended for you to set 200 as amplitude to avoid voltage saturation.
iv. Select Average number you want.
v. Make sure the cables are arranged appropriately (as shown above). vi. Press the Execute.
vii. Once the program report calibration finished. Check the saved log at RootLocation\[FINAL_SYDNEY]EIT_Mark25_20120202\Release\Cali bration\eit4\DCOffset\(CalibratedFrequency)KHz\DCOffset.txt to make sure calibration is successful.

### 2. Output Impedance calibration

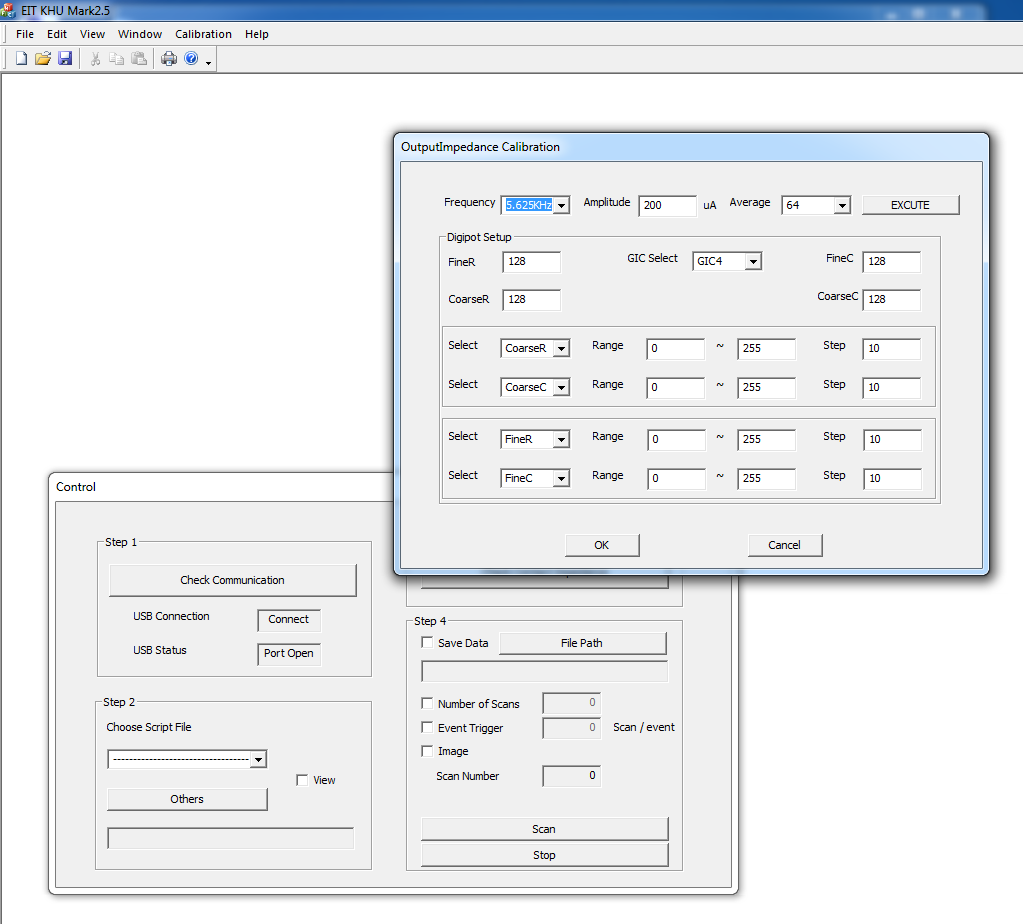
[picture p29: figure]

i. Select frequency you want to calibrate then GIC is changed automatically for the frequency range selected.
ii. Set current amplitude of waveform. Default value is 200uA. It is recommended for you to set 200 as amplitude to avoid voltage saturation.
iii. Select Average number you want.
iv. Do not change the value of any other boxes.
v. Make sure the cables are arranged appropriately (as shown above). vi. Press the Execute.
vii. Once the program report calibration finished. Check the saved log at RootLocation\[FINAL_SYDNEY]EIT_Mark25_20120202\Release\Cali bration\eit4\OutputImpedance\(CalibratedFrequency)KHz\OutputImpe dance.txt to make sure calibration is successful.

### 3. Amplitude calibration

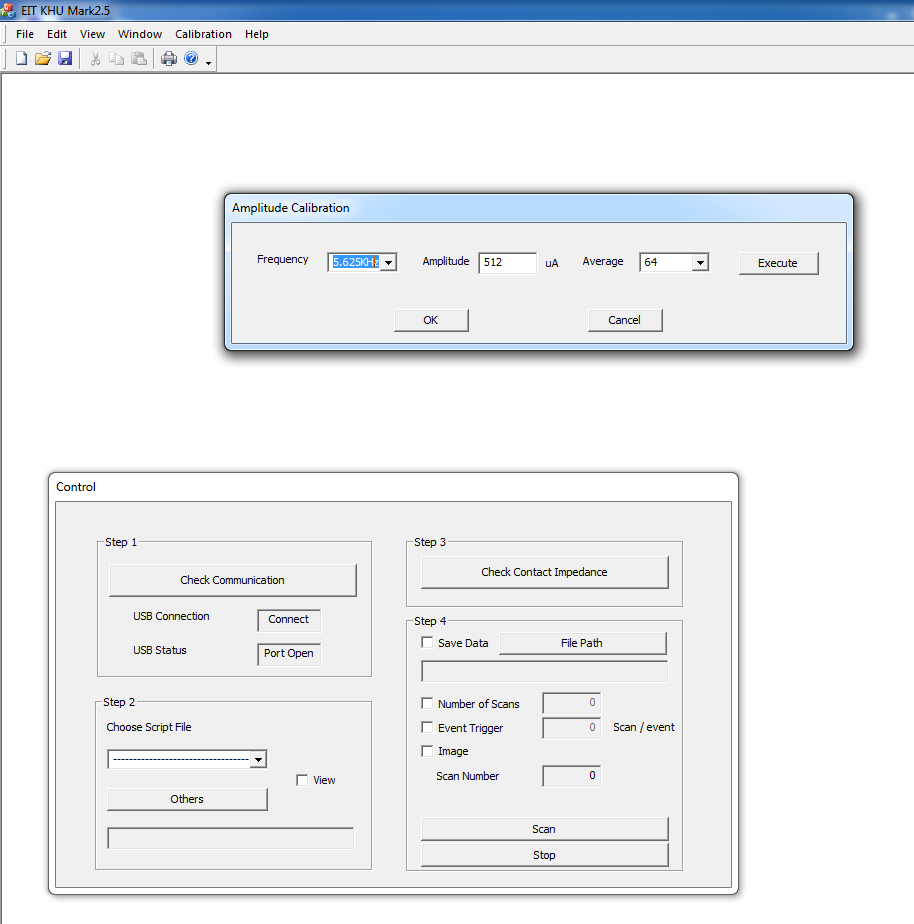
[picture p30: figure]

i. Select the frequency
ii. Set current amplitude of waveform. Default value is 512uA.
iii. Select Average number you want.
iv. Make sure the cables are arranged appropriately (as shown above).
v. Press the Execute.
vi. Once the program report calibration finished. Check the saved log at RootLocation\[FINAL_SYDNEY]EIT_Mark25_20120202\Release\Cali bration\eit4\Amplitude\(CalibratedFrequency)KHz\Amplitude.txt to make sure calibration is successful.

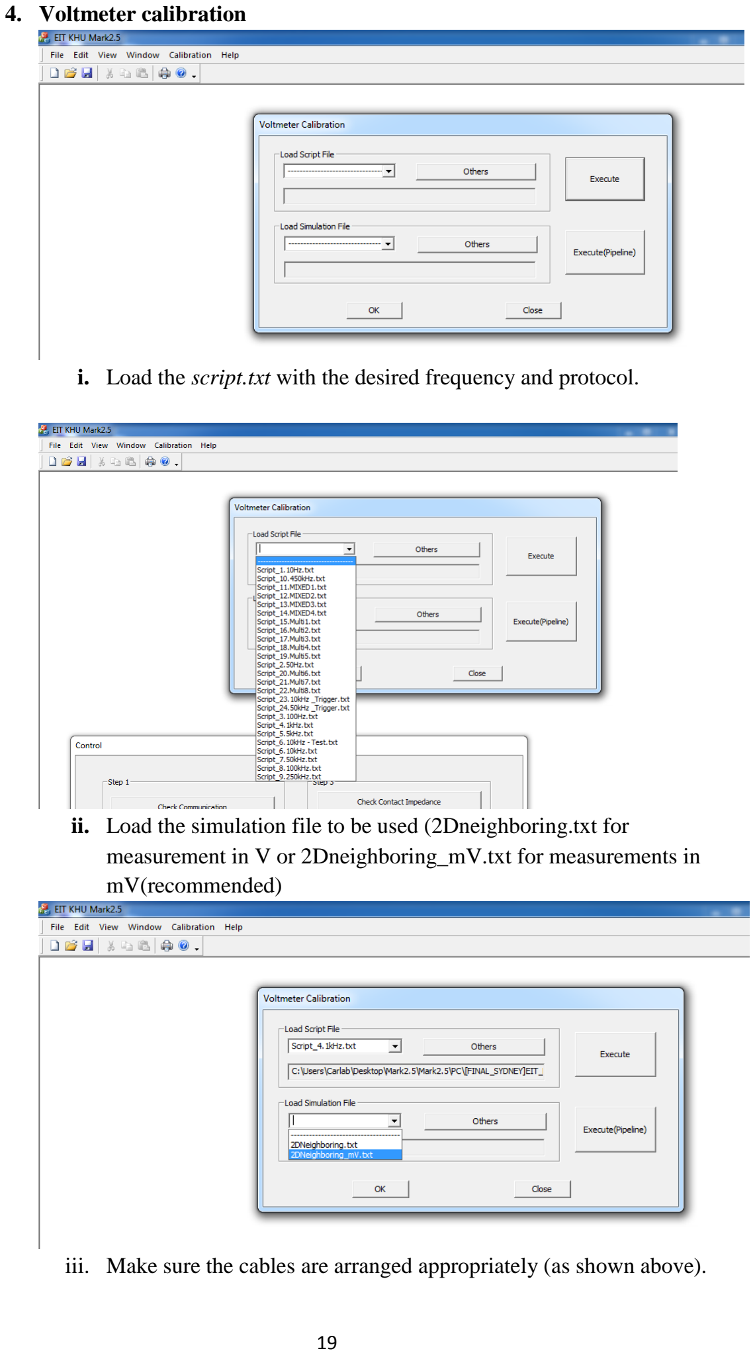
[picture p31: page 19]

### 4. Voltmeter calibration

i. Load the script.txt with the desired frequency and protocol.

ii. Load the simulation file to be used (2Dneighboring.txt for measurement in V or 2Dneighboring_mV.txt for measurements in mV(recommended)

iii. Make sure the cables are arranged appropriately (as shown above).

iv. Press the Execute for manual projection or Execute (Pipeline) for pipelining. Pipelining is the default setting of all normal scan, for which reason, we recommend using Execute(Pipeline) for calibration.
v. Once the program report calibration finished. Check the saved log at RootLocation\[FINAL_SYDNEY]EIT_Mark25_20120202\Release\Cali bration\eit4\Voltmeter\2DNeighboring(_mV)\ 2DNeighboring(_mV)_Script_(frequency)Hz_MagnitudeFacto.txt to make sure calibration is successful.

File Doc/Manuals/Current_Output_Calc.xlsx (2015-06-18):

 |  |  |  |  |  |  |  | Digital Value | current(mA) | voltage(V) | current(uA) p-p
 |  |  |  |  |  |  | Maximum | 1024 | 31.66 | 3.10268 | 1282.441067
 |  |  |  |  |  |  | Minimum | 0 | 8.66 | 0.84868 | 350.7877333
 |  |  |  |  |  |  | VALUE IN PROJECTION | 600 | 22.1365625 | 2.169383125 | 896.68
 |  |  |  |  |  |  | CURRENT LEVEL VALUE | 0
 |  |  |  |  |  |  |  |  | This maximum | In the IMM circuit | The voltage
 |  |  |  |  |  |  |  |  | and mimimum | after current is | signal is then
 |  |  |  |  |  |  |  |  | current is from the | generated from | converted to
 |  |  |  |  |  |  |  |  | DAC | the DAC, it is | current by howland current pump.
 |  |  |  |  |  |  |  |  |  | converted to voltage | This current value is calculated here
 |  |  |  |  |  |  |  |  |  | signal. This is | which will finally give you the
 |  |  |  |  |  |  |  |  |  | the resulting | output current in uA.
 |  |  |  |  |  |  |  |  |  | voltage.
Iout | = | R2 | / | R1 | x | Vin
 |  | R2B

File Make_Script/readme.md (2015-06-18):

## MAKE INJECTION SCRIPTS

The important one here is ``khu_makeprojectionfile.m`` which creates the script and projection files in the correct format for KHU control software to understand. Assumes single "pairwise" injections only

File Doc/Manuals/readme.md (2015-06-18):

# Manuals etc.

This folder contains all the supplementary info that KHU have sent us over the years

### Curent Output Calc
Shows the calculation from the digipot value on the HCP to the actual p-p current in uA

### EIT_Time_info_Calc
Explains what the ``TimeInfo`` setrings mean in the script file

### Projection table explanation
Details what bytes are sent to the IMMs, which are stored in ``ProjectionTableSendLog`` when saving data. These are used in khu_load to obtain the settings used

### KHU_MARK_2_Manual
Guide originally sent with system, pinch of salt requried

### James guide
Stuff learned over first few months of using/breaking/fixing the system

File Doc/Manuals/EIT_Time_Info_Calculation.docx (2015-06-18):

The equation to calculate time taken for 1 projection is:

T_(proj) =InjDelay+[({3+(AvgNum)+(DMDelay+1)})/(waveform frequency)]×S_(clk) ……….(i)

T_(scan) =Total Number ofProjections ×T_(proj) ………….(ii)

Where,

S_(clk) = system clock frequency = 45 MHz

DMDelay : is the delay in terms of cycles of the injection frequency = 0

AvgNum : is the number of averages used while acquiring the data. Minimum value is 1 and maximum is 64 and it must be a number which is power of 2.

InjDelay : This is the delay between the click of ‘Scan’ button and start of first scan = 60

T_(proj) = Time taken for 1 projection. This is the minimum time we can set. This value is obtained as number of cycles of the System clock frequency from the equation. Conversion to time unit (seconds) is explained below.

T_(scan) : Time taken for 1 scan.

For example,

For average number 64 and frequency = 10KHz,

After calculation from above equation , we get T_(proj) = 306060,

- This value should be converted to binary which is 1001010101110001100.
- Group this value in 4 bytes, i.e. → 00000000 00000100 10101011 10001100.
- Replace the last 8 bits as → 00000000 00000100 10101011 11111111.
- Now the 1st byte is TimeInfoHigh, 2nd is TimeInfoMid and 3rd is TimeInfoLow. So we would set TimeInfoHigh = 0, TimeInfoMid = 4, and TimeInfoLow = 171 in the script file.
- Again if we were to calculate T_(proj) in seconds, we must convert

00000000 00000100 10101011 11111111 to decimal which is 306175 and divide it by the clock frequency i.e., 45 MHz. So we get 6.8 ms which is the time taken for 1 projection.

So in order to set desired time taken for 1 projection, the values for TimeInfoHigh, TimeInfoMid and TimeInfoLow can be adjusted in the script file.

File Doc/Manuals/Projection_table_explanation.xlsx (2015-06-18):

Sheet: Projectiontable
ProjIndex | Ch | ChIndex | ChInfo | Inj.Freq | Amp1High | AmpLow | Amp2High | Amp2Low | Gain1 | AcqGap | AcqCNTHigh | AcqCntLow | TotalDMFreq | DM1 | DM2 | DM3
0 | 0 | 0 | 2 | 5 | 3 | 232 | 3 | 232 | 10 | 1 | 0 | 0 | 0 | 1 | 5 | 10
0 | 1 | 0 | 0 | 15 | 3 | 232 | 3 | 232 | 10 | 1 | 0 | 0 | 0 | 1 | 5 | 10
0 | 2 | 0 | 0 | 15 | 3 | 232 | 3 | 232 | 10 | 1 | 0 | 0 | 0 | 1 | 5 | 10
0 | 3 | 0 | 0 | 15 | 3 | 232 | 3 | 232 | 10 | 1 | 0 | 0 | 0 | 1 | 5 | 10
0 | 4 | 0 | 0 | 15 | 3 | 232 | 3 | 232 | 10 | 1 | 0 | 0 | 0 | 1 | 5 | 10
0 | 5 | 0 | 0 | 15 | 3 | 232 | 3 | 232 | 10 | 1 | 0 | 0 | 0 | 1 | 5 | 10
0 | 6 | 0 | 0 | 15 | 3 | 232 | 3 | 232 | 10 | 1 | 0 | 0 | 0 | 1 | 5 | 10
0 | 7 | 0 | 0 | 15 | 3 | 232 | 3 | 232 | 10 | 1 | 0 | 0 | 0 | 1 | 5 | 10
0 | 8 | 0 | 0 | 15 | 3 | 232 | 3 | 232 | 10 | 1 | 0 | 0 | 0 | 1 | 5 | 10
0 | 9 | 0 | 0 | 15 | 3 | 232 | 3 | 232 | 10 | 1 | 0 | 0 | 0 | 1 | 5 | 10
0 | 10 | 0 | 0 | 15 | 3 | 232 | 3 | 232 | 10 | 1 | 0 | 0 | 0 | 1 | 5 | 10
0 | 11 | 0 | 0 | 15 | 3 | 232 | 3 | 232 | 10 | 1 | 0 | 0 | 0 | 1 | 5 | 10
0 | 12 | 0 | 0 | 15 | 3 | 232 | 3 | 232 | 10 | 1 | 0 | 0 | 0 | 1 | 5 | 10
0 | 13 | 0 | 0 | 15 | 3 | 232 | 3 | 232 | 10 | 1 | 0 | 0 | 0 | 1 | 5 | 10
0 | 14 | 0 | 0 | 15 | 3 | 232 | 3 | 232 | 10 | 1 | 0 | 0 | 0 | 1 | 5 | 10
0 | 15 | 0 | 0 | 15 | 3 | 232 | 3 | 232 | 10 | 1 | 0 | 0 | 0 | 1 | 5 | 10
0 | 16 | 0 | 0 | 15 | 3 | 232 | 3 | 232 | 10 | 1 | 0 | 0 | 0 | 1 | 5 | 10
0 | 17 | 0 | 0 | 15 | 3 | 232 | 3 | 232 | 10 | 1 | 0 | 0 | 0 | 1 | 5 | 10
0 | 18 | 0 | 0 | 15 | 3 | 232 | 3 | 232 | 10 | 1 | 0 | 0 | 0 | 1 | 5 | 10
0 | 19 | 0 | 0 | 15 | 3 | 232 | 3 | 232 | 10 | 1 | 0 | 0 | 0 | 1 | 5 | 10
0 | 20 | 0 | 0 | 15 | 3 | 232 | 3 | 232 | 10 | 1 | 0 | 0 | 0 | 1 | 5 | 10
0 | 21 | 0 | 0 | 15 | 3 | 232 | 3 | 232 | 10 | 1 | 0 | 0 | 0 | 1 | 5 | 10
0 | 22 | 0 | 0 | 15 | 3 | 232 | 3 | 232 | 10 | 1 | 0 | 0 | 0 | 1 | 5 | 10
0 | 23 | 0 | 0 | 15 | 3 | 232 | 3 | 232 | 10 | 1 | 0 | 0 | 0 | 1 | 5 | 10
0 | 24 | 0 | 0 | 15 | 3 | 232 | 3 | 232 | 10 | 1 | 0 | 0 | 0 | 1 | 5 | 10
0 | 25 | 0 | 0 | 15 | 3 | 232 | 3 | 232 | 10 | 1 | 0 | 0 | 0 | 1 | 5 | 10
0 | 26 | 0 | 0 | 15 | 3 | 232 | 3 | 232 | 10 | 1 | 0 | 0 | 0 | 1 | 5 | 10
0 | 27 | 0 | 0 | 15 | 3 | 232 | 3 | 232 | 10 | 1 | 0 | 0 | 0 | 1 | 5 | 10
0 | 28 | 0 | 0 | 15 | 3 | 232 | 3 | 232 | 10 | 1 | 0 | 0 | 0 | 1 | 5 | 10
0 | 29 | 0 | 0 | 15 | 3 | 232 | 3 | 232 | 10 | 1 | 0 | 0 | 0 | 1 | 5 | 10
0 | 30 | 0 | 0 | 15 | 3 | 232 | 3 | 232 | 10 | 1 | 0 | 0 | 0 | 1 | 5 | 10
0 | 31 | 0 | 3 | 5 | 3 | 232 | 3 | 232 | 10 | 1 | 0 | 0 | 0 | 1 | 5 | 10
1 | 0 | 0 | 3 | 5 | 3 | 232 | 3 | 232 | 10 | 1 | 0 | 0 | 0 | 1 | 5 | 10
1 | 1 | 0 | 2 | 5 | 3 | 232 | 3 | 232 | 10 | 1 | 0 | 0 | 0 | 1 | 5 | 10
1 | 2 | 0 | 0 | 15 | 3 | 232 | 3 | 232 | 10 | 1 | 0 | 0 | 0 | 1 | 5 | 10
1 | 3 | 0 | 0 | 15 | 3 | 232 | 3 | 232 | 10 | 1 | 0 | 0 | 0 | 1 | 5 | 10
1 | 4 | 0 | 0 | 15 | 3 | 232 | 3 | 232 | 10 | 1 | 0 | 0 | 0 | 1 | 5 | 10
1 | 5 | 0 | 0 | 15 | 3 | 232 | 3 | 232 | 10 | 1 | 0 | 0 | 0 | 1 | 5 | 10
1 | 6 | 0 | 0 | 15 | 3 | 232 | 3 | 232 | 10 | 1 | 0 | 0 | 0 | 1 | 5 | 10
1 | 7 | 0 | 0 | 15 | 3 | 232 | 3 | 232 | 10 | 1 | 0 | 0 | 0 | 1 | 5 | 10
1 | 8 | 0 | 0 | 15 | 3 | 232 | 3 | 232 | 10 | 1 | 0 | 0 | 0 | 1 | 5 | 10
1 | 9 | 0 | 0 | 15 | 3 | 232 | 3 | 232 | 10 | 1 | 0 | 0 | 0 | 1 | 5 | 10
1 | 10 | 0 | 0 | 15 | 3 | 232 | 3 | 232 | 10 | 1 | 0 | 0 | 0 | 1 | 5 | 10
1 | 11 | 0 | 0 | 15 | 3 | 232 | 3 | 232 | 10 | 1 | 0 | 0 | 0 | 1 | 5 | 10
1 | 12 | 0 | 0 | 15 | 3 | 232 | 3 | 232 | 10 | 1 | 0 | 0 | 0 | 1 | 5 | 10
1 | 13 | 0 | 0 | 15 | 3 | 232 | 3 | 232 | 10 | 1 | 0 | 0 | 0 | 1 | 5 | 10
1 | 14 | 0 | 0 | 15 | 3 | 232 | 3 | 232 | 10 | 1 | 0 | 0 | 0 | 1 | 5 | 10
1 | 15 | 0 | 0 | 15 | 3 | 232 | 3 | 232 | 10 | 1 | 0 | 0 | 0 | 1 | 5 | 10
1 | 16 | 0 | 0 | 15 | 3 | 232 | 3 | 232 | 10 | 1 | 0 | 0 | 0 | 1 | 5 | 10
1 | 17 | 0 | 0 | 15 | 3 | 232 | 3 | 232 | 10 | 1 | 0 | 0 | 0 | 1 | 5 | 10
1 | 18 | 0 | 0 | 15 | 3 | 232 | 3 | 232 | 10 | 1 | 0 | 0 | 0 | 1 | 5 | 10
1 | 19 | 0 | 0 | 15 | 3 | 232 | 3 | 232 | 10 | 1 | 0 | 0 | 0 | 1 | 5 | 10
1 | 20 | 0 | 0 | 15 | 3 | 232 | 3 | 232 | 10 | 1 | 0 | 0 | 0 | 1 | 5 | 10
1 | 21 | 0 | 0 | 15 | 3 | 232 | 3 | 232 | 10 | 1 | 0 | 0 | 0 | 1 | 5 | 10
1 | 22 | 0 | 0 | 15 | 3 | 232 | 3 | 232 | 10 | 1 | 0 | 0 | 0 | 1 | 5 | 10
1 | 23 | 0 | 0 | 15 | 3 | 232 | 3 | 232 | 10 | 1 | 0 | 0 | 0 | 1 | 5 | 10
1 | 24 | 0 | 0 | 15 | 3 | 232 | 3 | 232 | 10 | 1 | 0 | 0 | 0 | 1 | 5 | 10
1 | 25 | 0 | 0 | 15 | 3 | 232 | 3 | 232 | 10 | 1 | 0 | 0 | 0 | 1 | 5 | 10
1 | 26 | 0 | 0 | 15 | 3 | 232 | 3 | 232 | 10 | 1 | 0 | 0 | 0 | 1 | 5 | 10
1 | 27 | 0 | 0 | 15 | 3 | 232 | 3 | 232 | 10 | 1 | 0 | 0 | 0 | 1 | 5 | 10
1 | 28 | 0 | 0 | 15 | 3 | 232 | 3 | 232 | 10 | 1 | 0 | 0 | 0 | 1 | 5 | 10
1 | 29 | 0 | 0 | 15 | 3 | 232 | 3 | 232 | 10 | 1 | 0 | 0 | 0 | 1 | 5 | 10
1 | 30 | 0 | 0 | 15 | 3 | 232 | 3 | 232 | 10 | 1 | 0 | 0 | 0 | 1 | 5 | 10
1 | 31 | 0 | 0 | 15 | 3 | 232 | 3 | 232 | 10 | 1 | 0 | 0 | 0 | 1 | 5 | 10
2 | 0 | 0 | 0 | 15 | 3 | 232 | 3 | 232 | 10 | 1 | 0 | 0 | 0 | 1 | 5 | 10
2 | 1 | 0 | 3 | 5 | 3 | 232 | 3 | 232 | 10 | 1 | 0 | 0 | 0 | 1 | 5 | 10
2 | 2 | 0 | 2 | 5 | 3 | 232 | 3 | 232 | 10 | 1 | 0 | 0 | 0 | 1 | 5 | 10
2 | 3 | 0 | 0 | 15 | 3 | 232 | 3 | 232 | 10 | 1 | 0 | 0 | 0 | 1 | 5 | 10
2 | 4 | 0 | 0 | 15 | 3 | 232 | 3 | 232 | 10 | 1 | 0 | 0 | 0 | 1 | 5 | 10
2 | 5 | 0 | 0 | 15 | 3 | 232 | 3 | 232 | 10 | 1 | 0 | 0 | 0 | 1 | 5 | 10
2 | 6 | 0 | 0 | 15 | 3 | 232 | 3 | 232 | 10 | 1 | 0 | 0 | 0 | 1 | 5 | 10
2 | 7 | 0 | 0 | 15 | 3 | 232 | 3 | 232 | 10 | 1 | 0 | 0 | 0 | 1 | 5 | 10
2 | 8 | 0 | 0 | 15 | 3 | 232 | 3 | 232 | 10 | 1 | 0 | 0 | 0 | 1 | 5 | 10
2 | 9 | 0 | 0 | 15 | 3 | 232 | 3 | 232 | 10 | 1 | 0 | 0 | 0 | 1 | 5 | 10
2 | 10 | 0 | 0 | 15 | 3 | 232 | 3 | 232 | 10 | 1 | 0 | 0 | 0 | 1 | 5 | 10
2 | 11 | 0 | 0 | 15 | 3 | 232 | 3 | 232 | 10 | 1 | 0 | 0 | 0 | 1 | 5 | 10
2 | 12 | 0 | 0 | 15 | 3 | 232 | 3 | 232 | 10 | 1 | 0 | 0 | 0 | 1 | 5 | 10
2 | 13 | 0 | 0 | 15 | 3 | 232 | 3 | 232 | 10 | 1 | 0 | 0 | 0 | 1 | 5 | 10
2 | 14 | 0 | 0 | 15 | 3 | 232 | 3 | 232 | 10 | 1 | 0 | 0 | 0 | 1 | 5 | 10
2 | 15 | 0 | 0 | 15 | 3 | 232 | 3 | 232 | 10 | 1 | 0 | 0 | 0 | 1 | 5 | 10
2 | 16 | 0 | 0 | 15 | 3 | 232 | 3 | 232 | 10 | 1 | 0 | 0 | 0 | 1 | 5 | 10
2 | 17 | 0 | 0 | 15 | 3 | 232 | 3 | 232 | 10 | 1 | 0 | 0 | 0 | 1 | 5 | 10
2 | 18 | 0 | 0 | 15 | 3 | 232 | 3 | 232 | 10 | 1 | 0 | 0 | 0 | 1 | 5 | 10
2 | 19 | 0 | 0 | 15 | 3 | 232 | 3 | 232 | 10 | 1 | 0 | 0 | 0 | 1 | 5 | 10
2 | 20 | 0 | 0 | 15 | 3 | 232 | 3 | 232 | 10 | 1 | 0 | 0 | 0 | 1 | 5 | 10
2 | 21 | 0 | 0 | 15 | 3 | 232 | 3 | 232 | 10 | 1 | 0 | 0 | 0 | 1 | 5 | 10
2 | 22 | 0 | 0 | 15 | 3 | 232 | 3 | 232 | 10 | 1 | 0 | 0 | 0 | 1 | 5 | 10
2 | 23 | 0 | 0 | 15 | 3 | 232 | 3 | 232 | 10 | 1 | 0 | 0 | 0 | 1 | 5 | 10
2 | 24 | 0 | 0 | 15 | 3 | 232 | 3 | 232 | 10 | 1 | 0 | 0 | 0 | 1 | 5 | 10
2 | 25 | 0 | 0 | 15 | 3 | 232 | 3 | 232 | 10 | 1 | 0 | 0 | 0 | 1 | 5 | 10
2 | 26 | 0 | 0 | 15 | 3 | 232 | 3 | 232 | 10 | 1 | 0 | 0 | 0 | 1 | 5 | 10
2 | 27 | 0 | 0 | 15 | 3 | 232 | 3 | 232 | 10 | 1 | 0 | 0 | 0 | 1 | 5 | 10
2 | 28 | 0 | 0 | 15 | 3 | 232 | 3 | 232 | 10 | 1 | 0 | 0 | 0 | 1 | 5 | 10
2 | 29 | 0 | 0 | 15 | 3 | 232 | 3 | 232 | 10 | 1 | 0 | 0 | 0 | 1 | 5 | 10
2 | 30 | 0 | 0 | 15 | 3 | 232 | 3 | 232 | 10 | 1 | 0 | 0 | 0 | 1 | 5 | 10
2 | 31 | 0 | 0 | 15 | 3 | 232 | 3 | 232 | 10 | 1 | 0 | 0 | 0 | 1 | 5 | 10
3 | 0 | 0 | 0 | 15 | 3 | 232 | 3 | 232 | 10 | 1 | 0 | 0 | 0 | 1 | 5 | 10
3 | 1 | 0 | 0 | 15 | 3 | 232 | 3 | 232 | 10 | 1 | 0 | 0 | 0 | 1 | 5 | 10
3 | 2 | 0 | 3 | 5 | 3 | 232 | 3 | 232 | 10 | 1 | 0 | 0 | 0 | 1 | 5 | 10
3 | 3 | 0 | 2 | 5 | 3 | 232 | 3 | 232 | 10 | 1 | 0 | 0 | 0 | 1 | 5 | 10
3 | 4 | 0 | 0 | 15 | 3 | 232 | 3 | 232 | 10 | 1 | 0 | 0 | 0 | 1 | 5 | 10
3 | 5 | 0 | 0 | 15 | 3 | 232 | 3 | 232 | 10 | 1 | 0 | 0 | 0 | 1 | 5 | 10
3 | 6 | 0 | 0 | 15 | 3 | 232 | 3 | 232 | 10 | 1 | 0 | 0 | 0 | 1 | 5 | 10
3 | 7 | 0 | 0 | 15 | 3 | 232 | 3 | 232 | 10 | 1 | 0 | 0 | 0 | 1 | 5 | 10
3 | 8 | 0 | 0 | 15 | 3 | 232 | 3 | 232 | 10 | 1 | 0 | 0 | 0 | 1 | 5 | 10
3 | 9 | 0 | 0 | 15 | 3 | 232 | 3 | 232 | 10 | 1 | 0 | 0 | 0 | 1 | 5 | 10
3 | 10 | 0 | 0 | 15 | 3 | 232 | 3 | 232 | 10 | 1 | 0 | 0 | 0 | 1 | 5 | 10
3 | 11 | 0 | 0 | 15 | 3 | 232 | 3 | 232 | 10 | 1 | 0 | 0 | 0 | 1 | 5 | 10
3 | 12 | 0 | 0 | 15 | 3 | 232 | 3 | 232 | 10 | 1 | 0 | 0 | 0 | 1 | 5 | 10
3 | 13 | 0 | 0 | 15 | 3 | 232 | 3 | 232 | 10 | 1 | 0 | 0 | 0 | 1 | 5 | 10
3 | 14 | 0 | 0 | 15 | 3 | 232 | 3 | 232 | 10 | 1 | 0 | 0 | 0 | 1 | 5 | 10
3 | 15 | 0 | 0 | 15 | 3 | 232 | 3 | 232 | 10 | 1 | 0 | 0 | 0 | 1 | 5 | 10
3 | 16 | 0 | 0 | 15 | 3 | 232 | 3 | 232 | 10 | 1 | 0 | 0 | 0 | 1 | 5 | 10
3 | 17 | 0 | 0 | 15 | 3 | 232 | 3 | 232 | 10 | 1 | 0 | 0 | 0 | 1 | 5 | 10
3 | 18 | 0 | 0 | 15 | 3 | 232 | 3 | 232 | 10 | 1 | 0 | 0 | 0 | 1 | 5 | 10
3 | 19 | 0 | 0 | 15 | 3 | 232 | 3 | 232 | 10 | 1 | 0 | 0 | 0 | 1 | 5 | 10
3 | 20 | 0 | 0 | 15 | 3 | 232 | 3 | 232 | 10 | 1 | 0 | 0 | 0 | 1 | 5 | 10
3 | 21 | 0 | 0 | 15 | 3 | 232 | 3 | 232 | 10 | 1 | 0 | 0 | 0 | 1 | 5 | 10
3 | 22 | 0 | 0 | 15 | 3 | 232 | 3 | 232 | 10 | 1 | 0 | 0 | 0 | 1 | 5 | 10
3 | 23 | 0 | 0 | 15 | 3 | 232 | 3 | 232 | 10 | 1 | 0 | 0 | 0 | 1 | 5 | 10
3 | 24 | 0 | 0 | 15 | 3 | 232 | 3 | 232 | 10 | 1 | 0 | 0 | 0 | 1 | 5 | 10
3 | 25 | 0 | 0 | 15 | 3 | 232 | 3 | 232 | 10 | 1 | 0 | 0 | 0 | 1 | 5 | 10
3 | 26 | 0 | 0 | 15 | 3 | 232 | 3 | 232 | 10 | 1 | 0 | 0 | 0 | 1 | 5 | 10
3 | 27 | 0 | 0 | 15 | 3 | 232 | 3 | 232 | 10 | 1 | 0 | 0 | 0 | 1 | 5 | 10
3 | 28 | 0 | 0 | 15 | 3 | 232 | 3 | 232 | 10 | 1 | 0 | 0 | 0 | 1 | 5 | 10
3 | 29 | 0 | 0 | 15 | 3 | 232 | 3 | 232 | 10 | 1 | 0 | 0 | 0 | 1 | 5 | 10
3 | 30 | 0 | 0 | 15 | 3 | 232 | 3 | 232 | 10 | 1 | 0 | 0 | 0 | 1 | 5 | 10
3 | 31 | 0 | 0 | 15 | 3 | 232 | 3 | 232 | 10 | 1 | 0 | 0 | 0 | 1 | 5 | 10
4 | 0 | 0 | 0 | 15 | 3 | 232 | 3 | 232 | 10 | 1 | 0 | 0 | 0 | 1 | 5 | 10
4 | 1 | 0 | 0 | 15 | 3 | 232 | 3 | 232 | 10 | 1 | 0 | 0 | 0 | 1 | 5 | 10
4 | 2 | 0 | 0 | 15 | 3 | 232 | 3 | 232 | 10 | 1 | 0 | 0 | 0 | 1 | 5 | 10
4 | 3 | 0 | 3 | 5 | 3 | 232 | 3 | 232 | 10 | 1 | 0 | 0 | 0 | 1 | 5 | 10
4 | 4 | 0 | 2 | 5 | 3 | 232 | 3 | 232 | 10 | 1 | 0 | 0 | 0 | 1 | 5 | 10
4 | 5 | 0 | 0 | 15 | 3 | 232 | 3 | 232 | 10 | 1 | 0 | 0 | 0 | 1 | 5 | 10
4 | 6 | 0 | 0 | 15 | 3 | 232 | 3 | 232 | 10 | 1 | 0 | 0 | 0 | 1 | 5 | 10
4 | 7 | 0 | 0 | 15 | 3 | 232 | 3 | 232 | 10 | 1 | 0 | 0 | 0 | 1 | 5 | 10
4 | 8 | 0 | 0 | 15 | 3 | 232 | 3 | 232 | 10 | 1 | 0 | 0 | 0 | 1 | 5 | 10
4 | 9 | 0 | 0 | 15 | 3 | 232 | 3 | 232 | 10 | 1 | 0 | 0 | 0 | 1 | 5 | 10
4 | 10 | 0 | 0 | 15 | 3 | 232 | 3 | 232 | 10 | 1 | 0 | 0 | 0 | 1 | 5 | 10
4 | 11 | 0 | 0 | 15 | 3 | 232 | 3 | 232 | 10 | 1 | 0 | 0 | 0 | 1 | 5 | 10
4 | 12 | 0 | 0 | 15 | 3 | 232 | 3 | 232 | 10 | 1 | 0 | 0 | 0 | 1 | 5 | 10
4 | 13 | 0 | 0 | 15 | 3 | 232 | 3 | 232 | 10 | 1 | 0 | 0 | 0 | 1 | 5 | 10
4 | 14 | 0 | 0 | 15 | 3 | 232 | 3 | 232 | 10 | 1 | 0 | 0 | 0 | 1 | 5 | 10
4 | 15 | 0 | 0 | 15 | 3 | 232 | 3 | 232 | 10 | 1 | 0 | 0 | 0 | 1 | 5 | 10
4 | 16 | 0 | 0 | 15 | 3 | 232 | 3 | 232 | 10 | 1 | 0 | 0 | 0 | 1 | 5 | 10
4 | 17 | 0 | 0 | 15 | 3 | 232 | 3 | 232 | 10 | 1 | 0 | 0 | 0 | 1 | 5 | 10
4 | 18 | 0 | 0 | 15 | 3 | 232 | 3 | 232 | 10 | 1 | 0 | 0 | 0 | 1 | 5 | 10
4 | 19 | 0 | 0 | 15 | 3 | 232 | 3 | 232 | 10 | 1 | 0 | 0 | 0 | 1 | 5 | 10
4 | 20 | 0 | 0 | 15 | 3 | 232 | 3 | 232 | 10 | 1 | 0 | 0 | 0 | 1 | 5 | 10
4 | 21 | 0 | 0 | 15 | 3 | 232 | 3 | 232 | 10 | 1 | 0 | 0 | 0 | 1 | 5 | 10
4 | 22 | 0 | 0 | 15 | 3 | 232 | 3 | 232 | 10 | 1 | 0 | 0 | 0 | 1 | 5 | 10
4 | 23 | 0 | 0 | 15 | 3 | 232 | 3 | 232 | 10 | 1 | 0 | 0 | 0 | 1 | 5 | 10
4 | 24 | 0 | 0 | 15 | 3 | 232 | 3 | 232 | 10 | 1 | 0 | 0 | 0 | 1 | 5 | 10
4 | 25 | 0 | 0 | 15 | 3 | 232 | 3 | 232 | 10 | 1 | 0 | 0 | 0 | 1 | 5 | 10
4 | 26 | 0 | 0 | 15 | 3 | 232 | 3 | 232 | 10 | 1 | 0 | 0 | 0 | 1 | 5 | 10
4 | 27 | 0 | 0 | 15 | 3 | 232 | 3 | 232 | 10 | 1 | 0 | 0 | 0 | 1 | 5 | 10
4 | 28 | 0 | 0 | 15 | 3 | 232 | 3 | 232 | 10 | 1 | 0 | 0 | 0 | 1 | 5 | 10
4 | 29 | 0 | 0 | 15 | 3 | 232 | 3 | 232 | 10 | 1 | 0 | 0 | 0 | 1 | 5 | 10
4 | 30 | 0 | 0 | 15 | 3 | 232 | 3 | 232 | 10 | 1 | 0 | 0 | 0 | 1 | 5 | 10
4 | 31 | 0 | 0 | 15 | 3 | 232 | 3 | 232 | 10 | 1 | 0 | 0 | 0 | 1 | 5 | 10
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

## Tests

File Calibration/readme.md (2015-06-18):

# THIS HAS NOT BEEN TESTED THOUROUGHLY

OK? Seriously.

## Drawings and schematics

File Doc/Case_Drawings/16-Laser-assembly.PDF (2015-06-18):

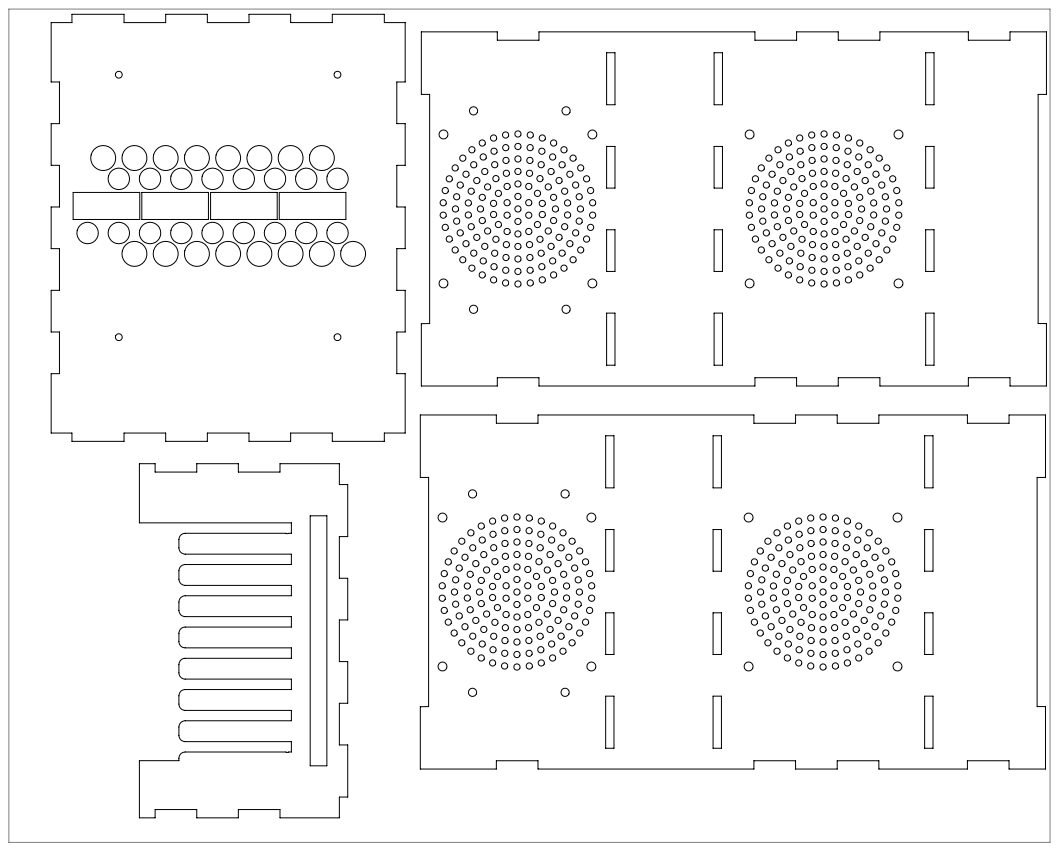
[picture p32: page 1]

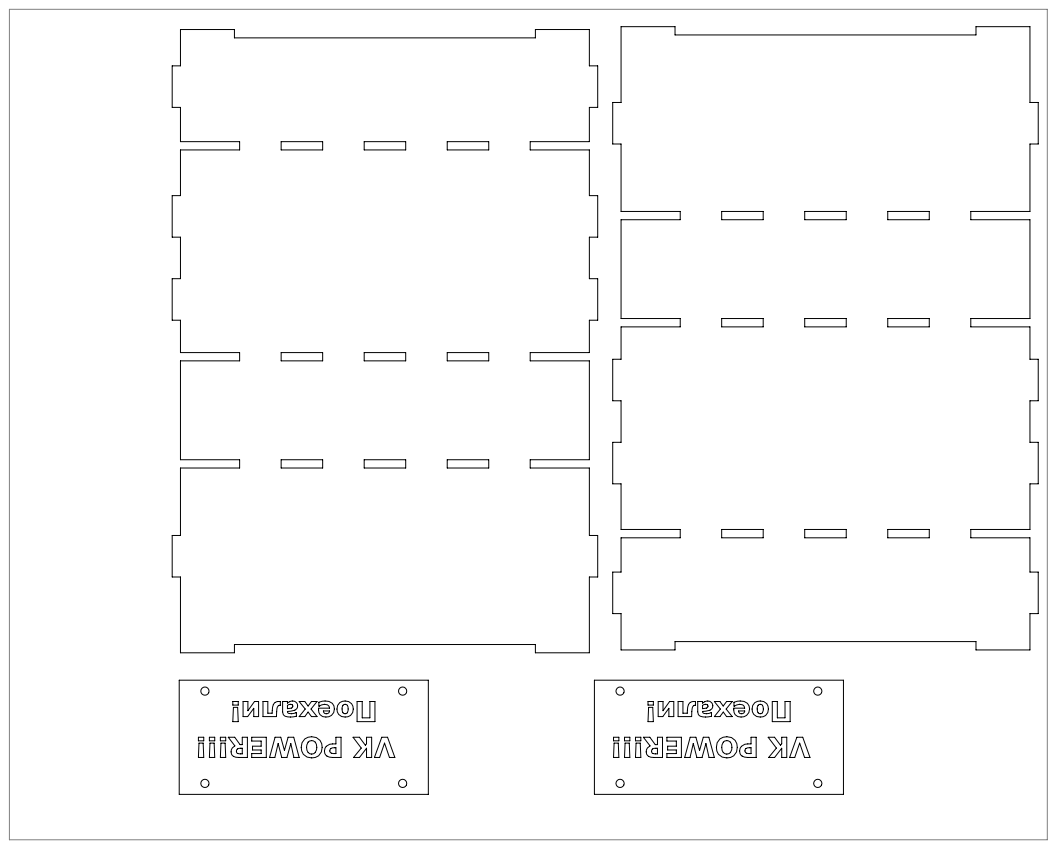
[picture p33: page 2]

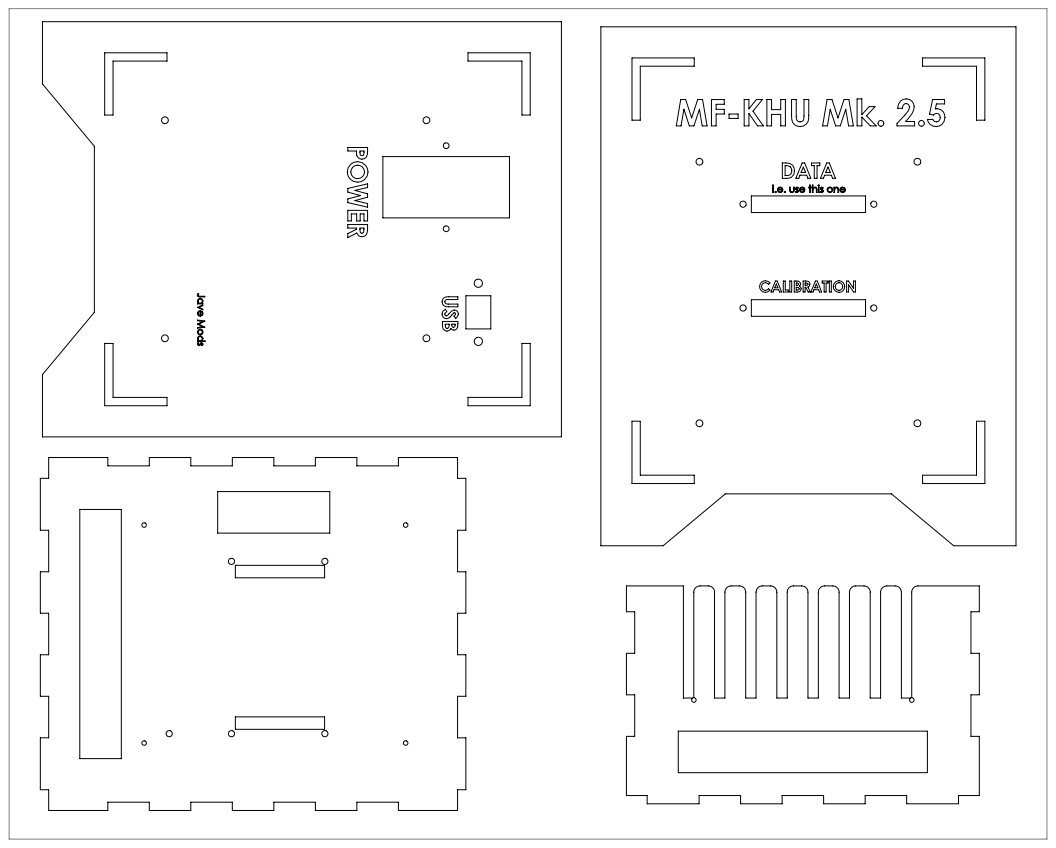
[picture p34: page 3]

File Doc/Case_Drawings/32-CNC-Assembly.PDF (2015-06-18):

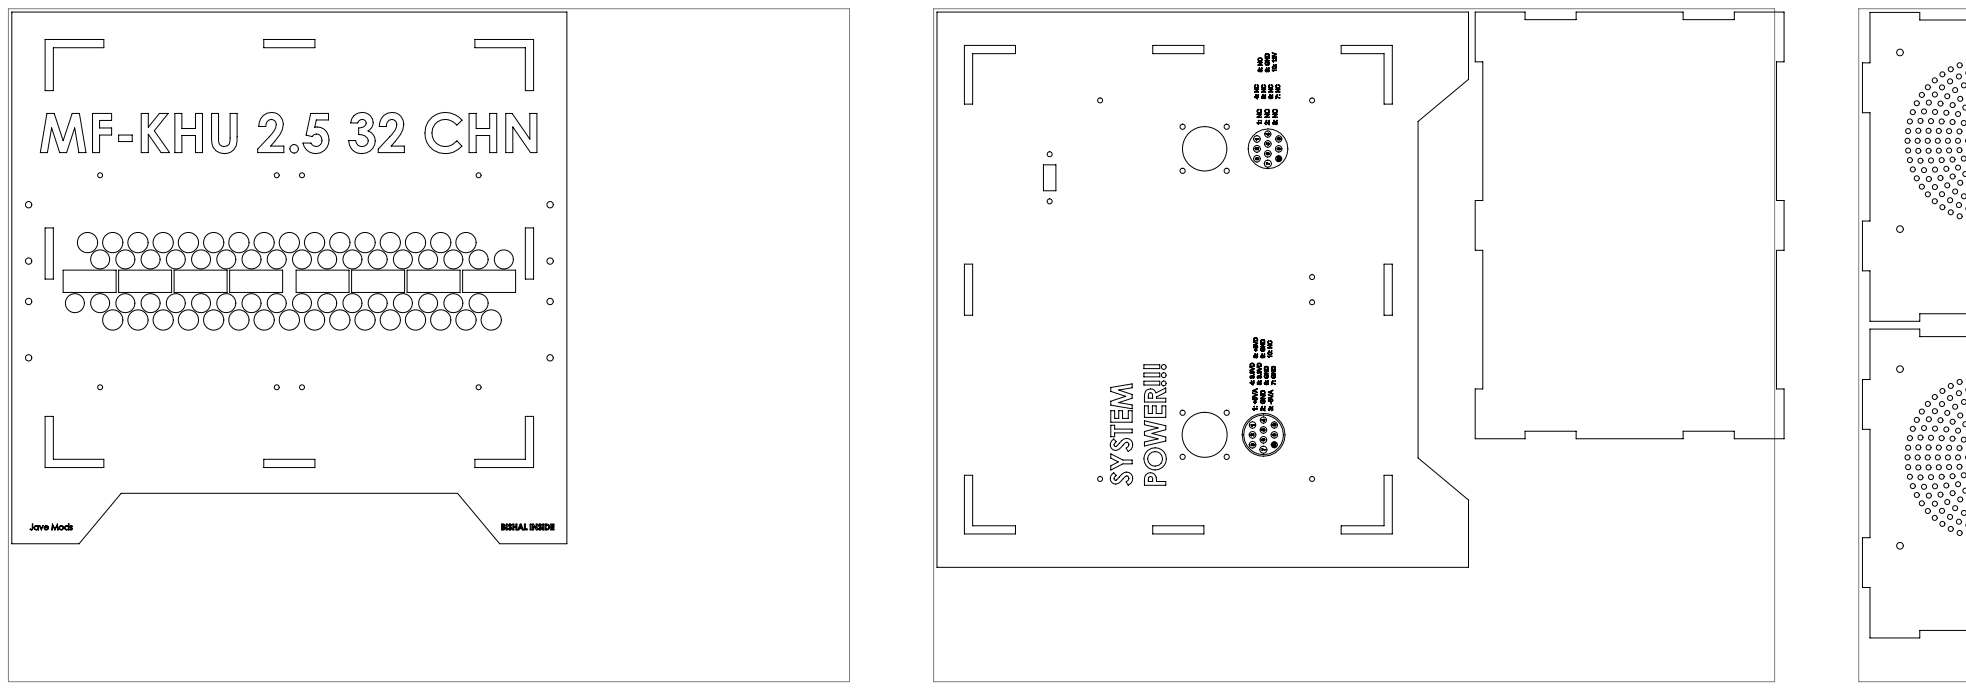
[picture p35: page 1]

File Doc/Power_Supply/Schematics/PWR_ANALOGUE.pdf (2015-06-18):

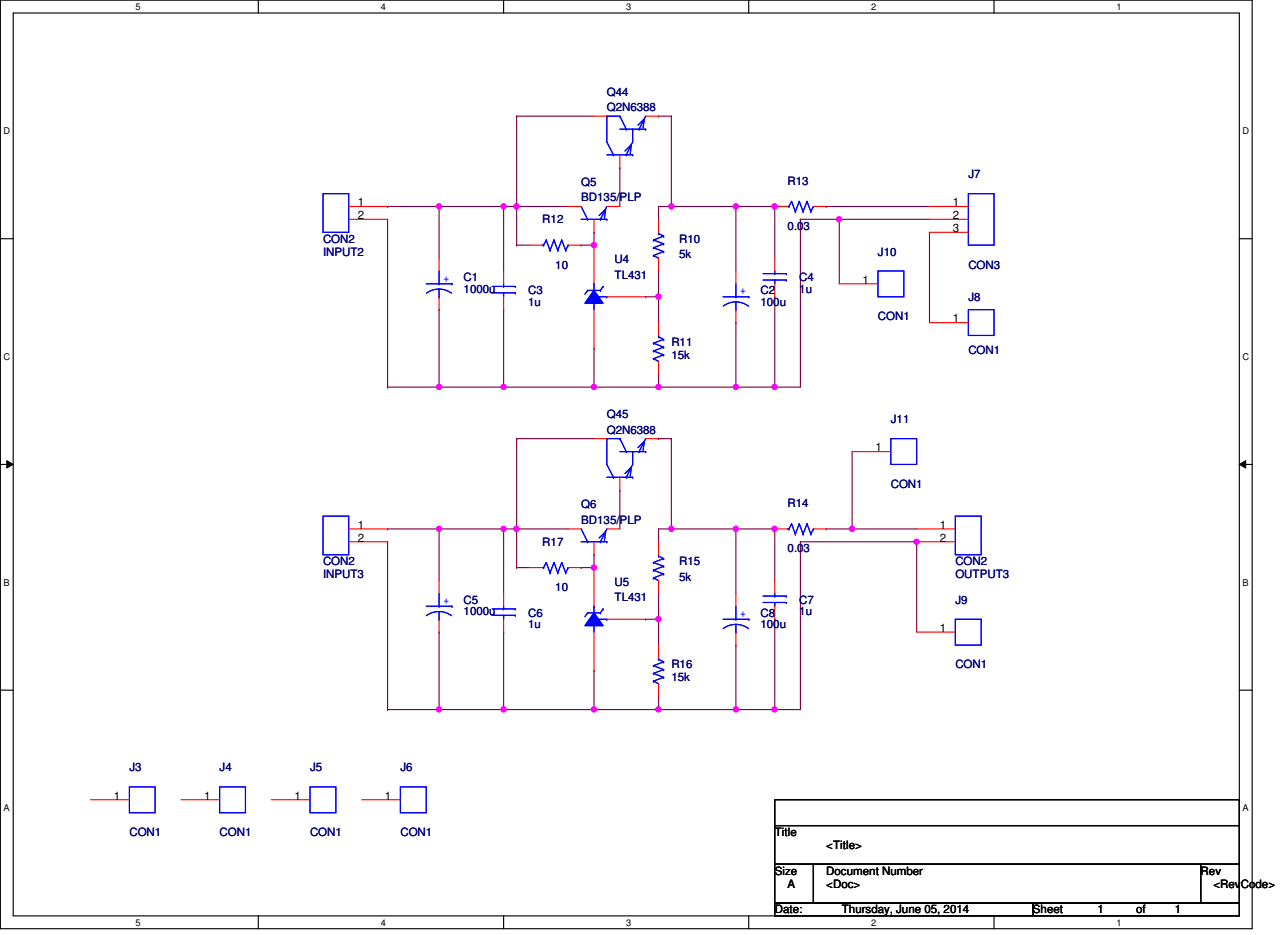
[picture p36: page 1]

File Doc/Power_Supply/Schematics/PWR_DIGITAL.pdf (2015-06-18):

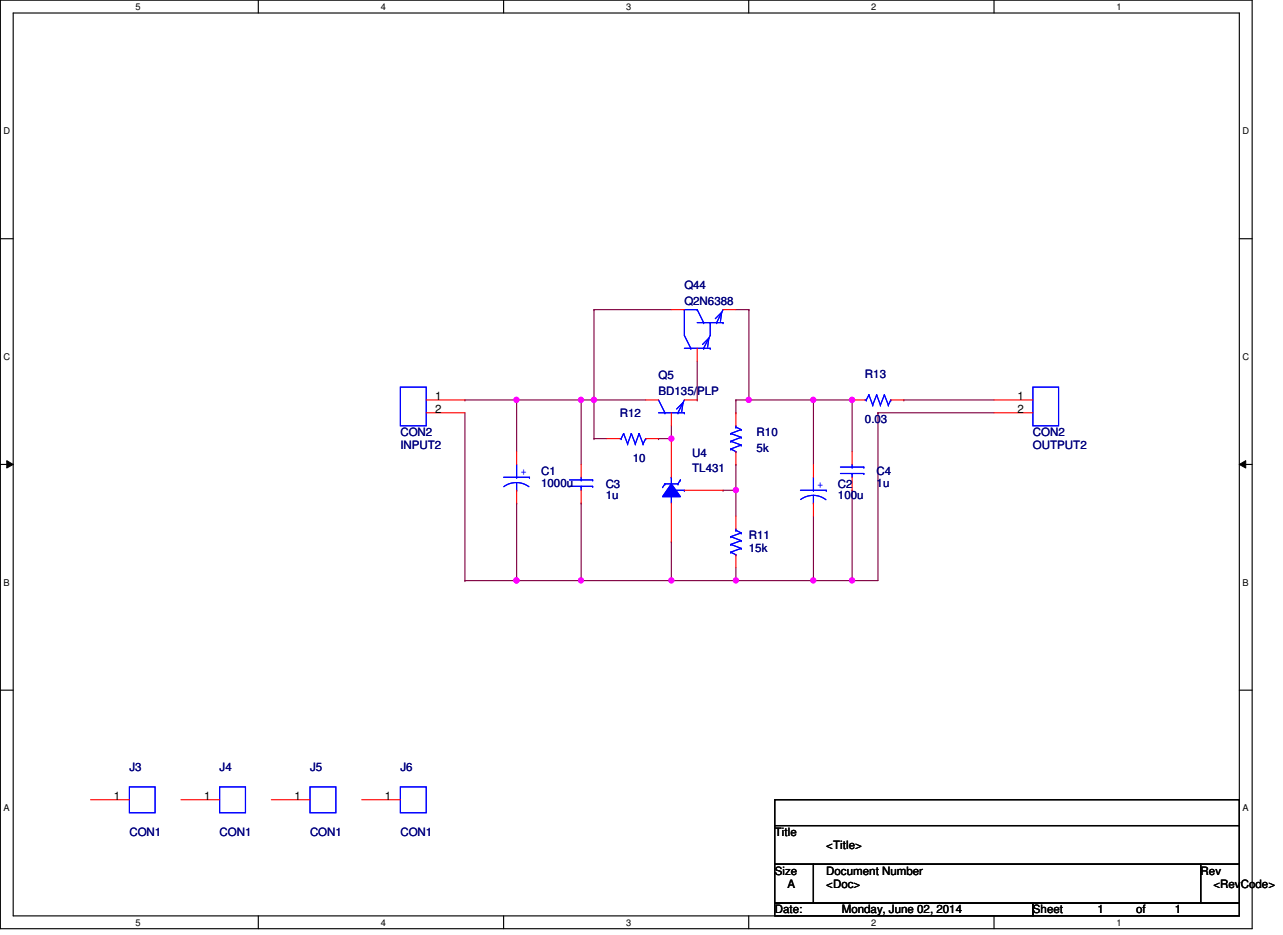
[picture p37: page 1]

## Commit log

2015-06-18 Added Case Models and Drawings and Power Supply Schematics
    [32PowerCaseCNR.STEP, 32PowerCaseCNR.STL]
2015-06-18 Added more manuals and guides
    [Current_Output_Calc.xlsx, Projection_table_explanation.xlsx]
2015-06-22 Added allegro versions of schematics
    [32CH_PWR_ANALOGUE.brd, 32CH_PWR_DIGITAL.brd, xpreg.dsn]
2015-06-22 more name changing
    [xpreg.dsn]
2015-06-24 added Resisor Phantom Designs and work version of JAMES guide
    [RESISTERPHANTOM(SIMUL).DSN, RESISTERPHANTOM.DSN]
